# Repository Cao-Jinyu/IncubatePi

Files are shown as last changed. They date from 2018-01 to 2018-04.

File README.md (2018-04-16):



### Neonate (Newborn Child) Real Time Temperature Control Incubator

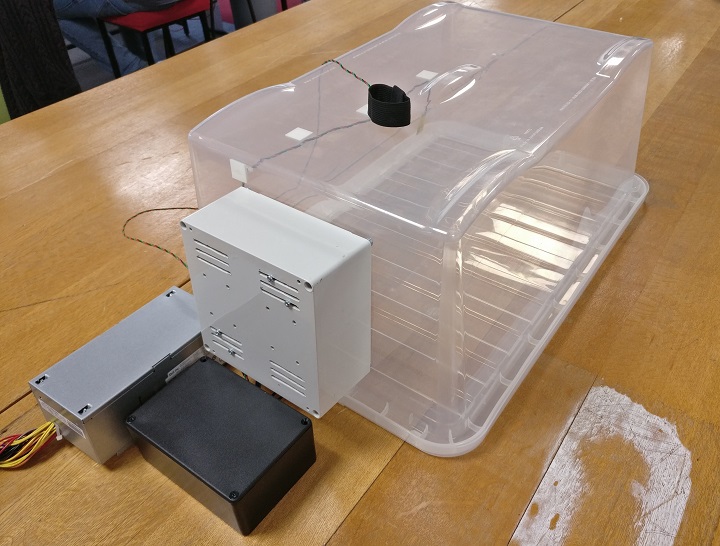
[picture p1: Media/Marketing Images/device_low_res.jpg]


*Features a Raspberry Pi, Temperature Sensors, a Heater and a Fan.*  
*Low budget alternative to conventional incubators suitable for the developing world.*

**Find our promotional video on YouTube:** http://www.youtube.com/watch?v=8vy_HCOcaGk  
**You can also find a demonstration of the device here:** https://www.youtube.com/watch?v=y4fZthFY24Q

[facebook_icon]: https://raw.githubusercontent.com/croaljack0/IncubatePi/master/Media/Marketing%20Images/facebook_icon.png
[facebook_url]: https://www.facebook.com/IncuPi/
[instagram_icon]: https://raw.githubusercontent.com/croaljack0/IncubatePi/master/Media/Marketing%20Images/instagram_icon.png
[instagram_url]: https://www.instagram.com/incupi_project
[youtube_icon]: https://raw.githubusercontent.com/croaljack0/IncubatePi/master/Media/Marketing%20Images/youtube_icon.png
[youtube_url]: https://www.youtube.com/channel/UCyrm2wJSCseUDFAKD9X7mjQ
Click these icons to follow us on  [][facebook_url] &nbsp; [][instagram_url] &nbsp; [][youtube_url]

View our project on Hackaday: https://hackaday.io/project/125376-incupi

## Problem

Premature or ill neonates often require automated temperature monitoring and control because they are unable to properly regulate their own body temperature. This is conventionally provided using expensive incubator systems. In the developing world, where standards of health care are poor and funding is very limited, an incubator solution using inexpensive and widely accessible technology is required.

## Solution

IncuPi provides a neonate temperature monitoring solution using a Raspberry Pi as the central control unit. Multiple temperature sensors provide information about the temperature of the neonate and the incubator ambient temperature. Embedded PID control software on the Raspberry Pi is then used to control a heater and fan system. This provides the appropriate heat control to ensure a neonate body temperature of 37 degrees Celsius.

**SEE THE WIKI DOCS [HERE](https://github.com/croaljack0/IncubatePi/wiki) FOR DETAILED HARDWARE AND SOFTWARE IMPLEMENTATION**

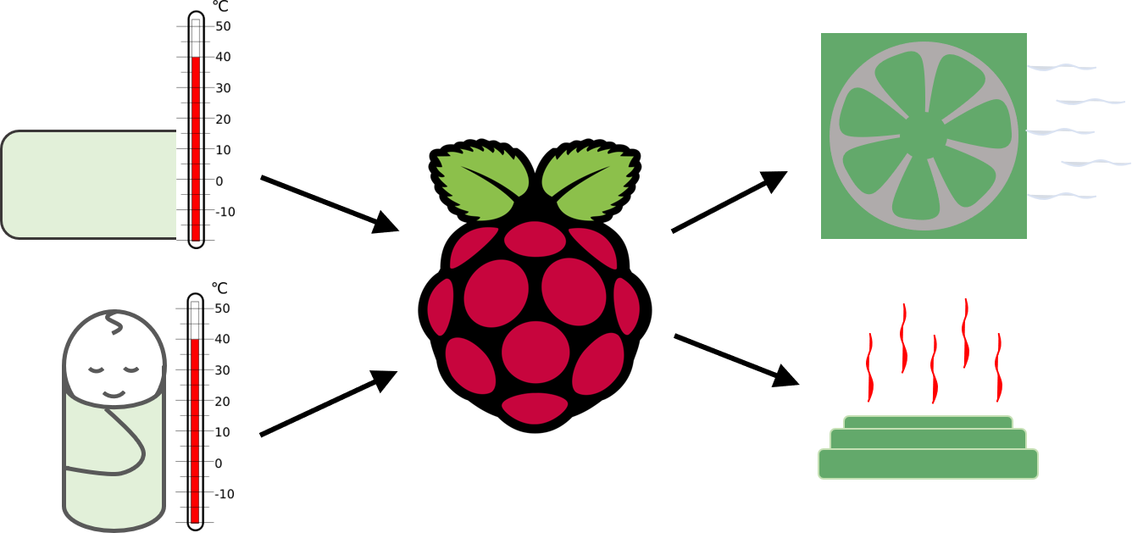
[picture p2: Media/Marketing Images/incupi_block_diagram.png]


## Real-time evaluation

#### 1. Responsiveness of the application
A fast temperature response was required to ensure fast-heating of the incubator in emergency situations. The final device was successful in achieving this. The PID temperature response times are shown below:

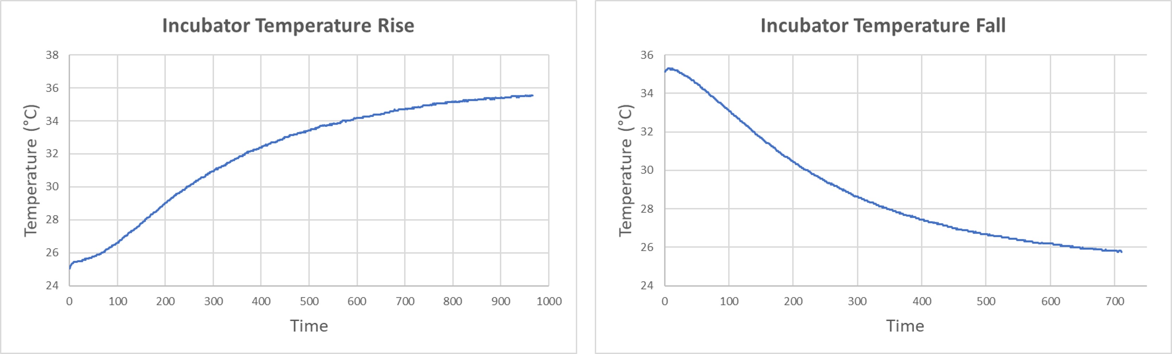
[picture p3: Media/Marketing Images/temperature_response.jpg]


The full data for these results can be found [HERE](./Experimental%20Data).

#### 2. Permitted latencies
The latency between the temperature reading and the incubator temperature change has been tested to be no longer than one minute for temperature changes of one degree Celsius.

#### 3. Sampling rate
The ambient temperature of the incubator is sampled and processed every 10 seconds by the PID control software. The neonate temperature is sampled every minute because this temperature does not vary significantly over short periods of time. This ensures sufficient data for the temperature control, modifying the heater/fan power every 5 seconds.

#### 4. Bus protocol
The Raspberry Pi communicates with the DS18B20 temperature sensors using the RPI's 1-wire interface. This uses a single wire to provide data, and power. This reduces wiring complexity and allows for multiple temperature devices connected in parallel without a chip select line for each, thus improving the flexibility and scalability.

A standard PWM signal is used to control the fan.

#### 5. How many channels
Multiple temperature sensor channels can be connected to the Raspberry Pi using the 1-wire interface. The default for this is 2: one for neonate temperature and one for the incubator ambient temperature. This is passed to the GPIO and PWM outputs to control the heating element's MOSFET and the fan respectively.

#### 6. Low level implementation: kernel or user space?
The main application runs in user space because it provides security and portability. The timing requirements of the system were not severe enough to warrant custom kernel routines. Some of the external interfaces (eg. 1-wire) are implemented using loadable kernel modules.

#### 7. Data flow from hardware to GUI to output
The Raspberry Pi sends data to a connected monitor, using QT for the display output. The Raspberry Pi is connected to the monitor using it's built-in VGA connection with an HDMI adapter.

#### 8. Buffering of data
The temperature data is buffered over a maximum of 5 minutes to aid in the accurate PID control of the slow-changing temperature values.

#### 9. Buffering impacting on the real-time performance
The buffering of the temperature values is a low performance activity, and introduces very little latency within the application.

#### 10. Post-processing of data, latencies and processor load
The data is processed real-time as the temperature information is detected. This is post-processed in by the custom PID controller to provide the values for the heater and fan elements. This introduces a maximum latency of 5 ms, allowing for low-latency temperature changes.

#### 11. Number of threads and load be distribution
The main software is executed in one thread, and child threads are created to handle the temperature measurements and other external interrupts. The number of child threads created can be varied depending on the number of temperature sensors connected, to aid in the scalability of the application.

#### 12. GUI implementation
The GUI is implemented using QT, and is displayed on a connected monitor. The refresh rate is equal to the temperature sensor sample rate: refresh every second. The allowed latency is 0.5 seconds. The temperature information is displayed real-time, along with the PID temperature controller data. This can be viewed in the [Software wiki](https://github.com/croaljack0/IncubatePi/wiki/Software).

#### 13. Class structure and unit tests
The software features a main class and 4 other classes as follows:

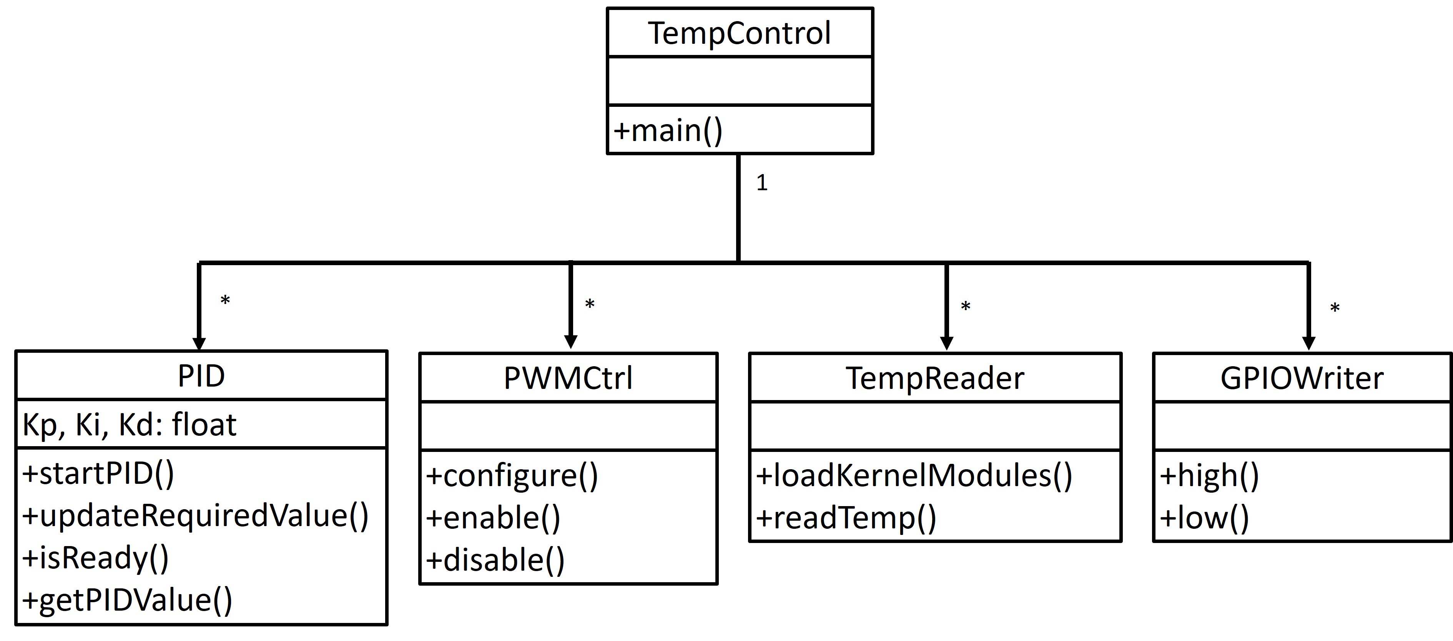
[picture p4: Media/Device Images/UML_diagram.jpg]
UML diagram


Unit tests are included for each class, and can be executed using the command `make test` within the software directory.

**SEE THE WIKI DOCS FOR DETAILS ON SOFTWARE [HERE](https://github.com/croaljack0/IncubatePi/wiki/Software)**

#### 14. Team structure
The team members and roles are as follows:

* **Jack Croal** - Hardware Developer
* **Chris Brown** - Software Developer
* **Cameron Houston** - GUI Implementation

These roles are flexible, with every team member cooperating on each section of the project to improve the common understanding within the team. Three times weekly scrum meetings are carried out to establish roles and tasks.

#### 15. Project time allocation
This project was completed over 4 months.

* **January**: Research and initial experimental development
* **February**: Hardware manufacturing and software implementation
* **March**: Finalising of software and incubator experimental tests
* **April**: Completion of project with release and media engagement

#### 16. Version control
The git version control software was chosen due to its wide-scale use and support, and its ability to merge between branches and create releases. The software releases can be found in the [releases section](https://github.com/croaljack0/IncubatePi/releases) of this GitHub, labeled A.B where A is the major release number and B is the minor release number.

#### 17. Release strategy and publication
[facebook_icon]: https://raw.githubusercontent.com/croaljack0/IncubatePi/master/Media/Marketing%20Images/facebook_icon.png
[facebook_url]: https://www.facebook.com/IncuPi/
[instagram_icon]: https://raw.githubusercontent.com/croaljack0/IncubatePi/master/Media/Marketing%20Images/instagram_icon.png
[instagram_url]: https://www.instagram.com/incupi_project
[youtube_icon]: https://raw.githubusercontent.com/croaljack0/IncubatePi/master/Media/Marketing%20Images/youtube_icon.png
[youtube_url]: https://www.youtube.com/channel/UCyrm2wJSCseUDFAKD9X7mjQ
Click these icons to follow us on  [][facebook_url] &nbsp; [][instagram_url] &nbsp; [][youtube_url]

The project can also be found on Hackaday here: https://hackaday.io/project/125376-incupi

The software and hardware schematics are released here on GitHub. Please feel free to download, under the MIT license included.

#### 18. Success of the application
The application is evaluated on its temperature response time based on the neonate's temperature changes. The experimental results are included [HERE](./Experimental%20Data). The application is successful in holding a steady temperature within the incubator and changes the temperature accordingly with low latency and useful graphical output.

Overall, this project demonstrates a key understanding of real-time applications, and follows a clear software life-cycle using proper software development techniques.

## University of Glasgow
Developed as part of Real Time Embedded Programming Project at the University of Glasgow.

Course convener:    Dr Bernd Porr

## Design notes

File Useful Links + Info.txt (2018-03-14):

Incubator Information:
http://www.d4surgicals.com/Infant-Incubator/index.htm

Adafruit temperature sensor document
https://cdn-learn.adafruit.com/downloads/pdf/adafruits-raspberry-pi-lesson-11-ds18b20-temperature-sensing.pdf

http://www.jumpnowtek.com/rpi/Using-the-Raspberry-Pi-Hardware-PWM-timers.html

http://librpip.frasersdev.net/peripheral-config/pwm0and1/

https://sites.google.com/site/semilleroadt/raspberry-pi-tutorials/gpio

ssh -X team10@rank510iot.eng.gla.ac.uk

ssh -X pi@192.168.1.181

git config --global http.proxy http://wwwcache.gla.ac.uk:8080

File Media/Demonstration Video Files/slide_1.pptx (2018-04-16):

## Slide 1

FINAL DEVICE
      - Heating Element
      - Fan
      - Temperature Sensors
      - Modular Enclosures

A picture containing object Description generated with very high confidence

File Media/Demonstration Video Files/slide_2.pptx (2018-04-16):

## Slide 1

PWM Fan Operation
- Adjusts automatically to temperature fluctuations
- Disperses heat through incubator

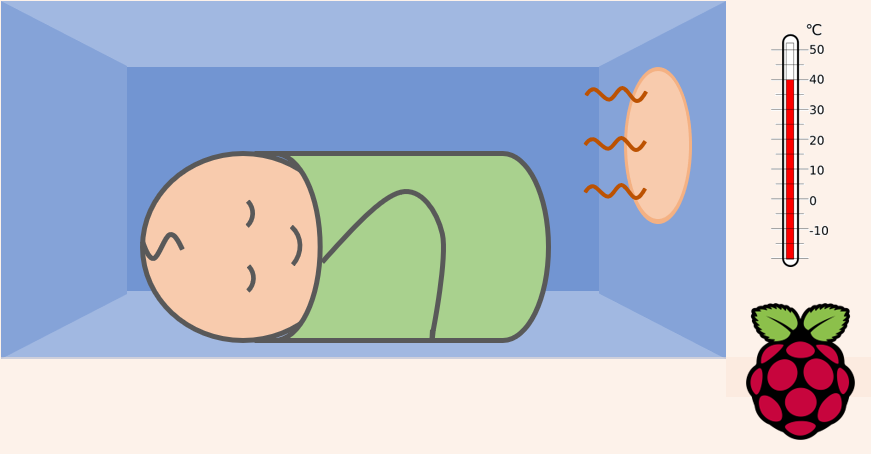
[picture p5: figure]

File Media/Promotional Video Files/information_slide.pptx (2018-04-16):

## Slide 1

For more information:
Follow IncuPi on and
Find our GitHub repository for source code
and device construction:
https://github.com/croaljack0/IncubatePi

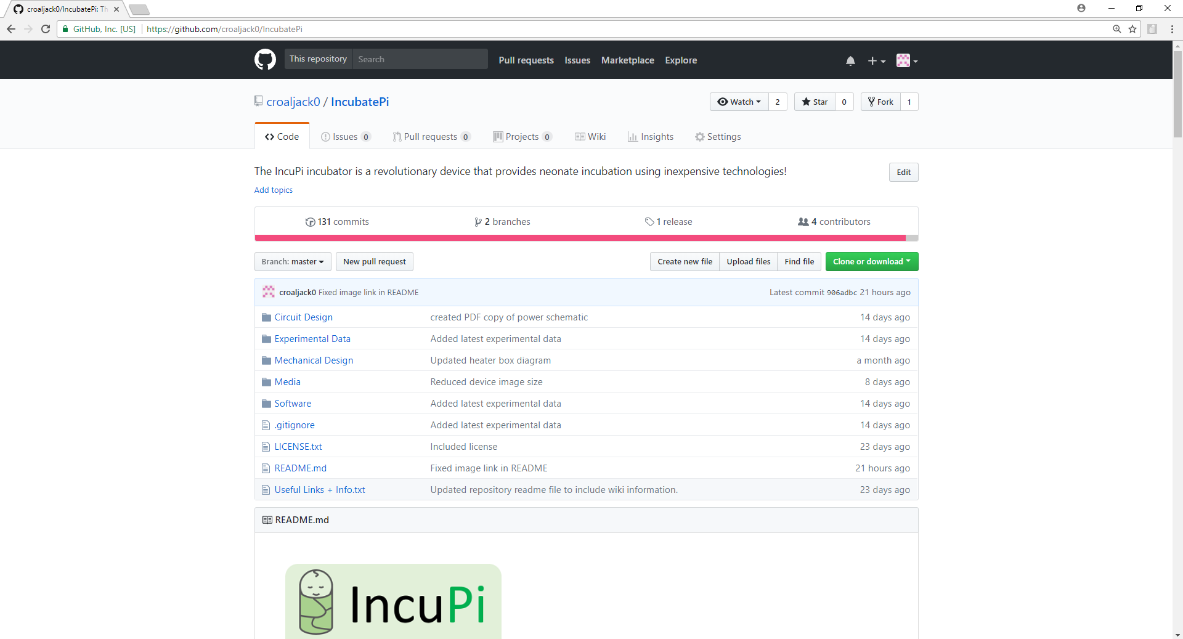
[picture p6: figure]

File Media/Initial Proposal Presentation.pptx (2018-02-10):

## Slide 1

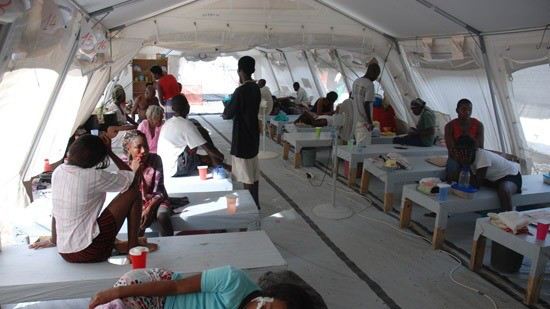
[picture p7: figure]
Image result for third world medicine

IncuPi

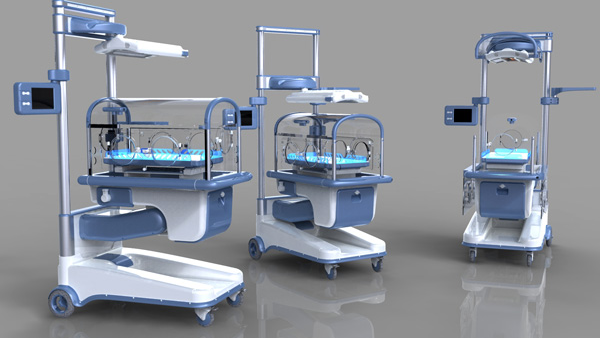
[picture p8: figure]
Image result for incubator neonate

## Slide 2

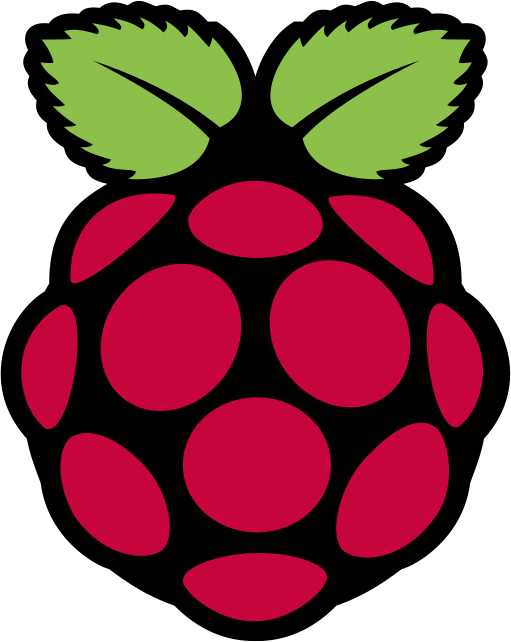
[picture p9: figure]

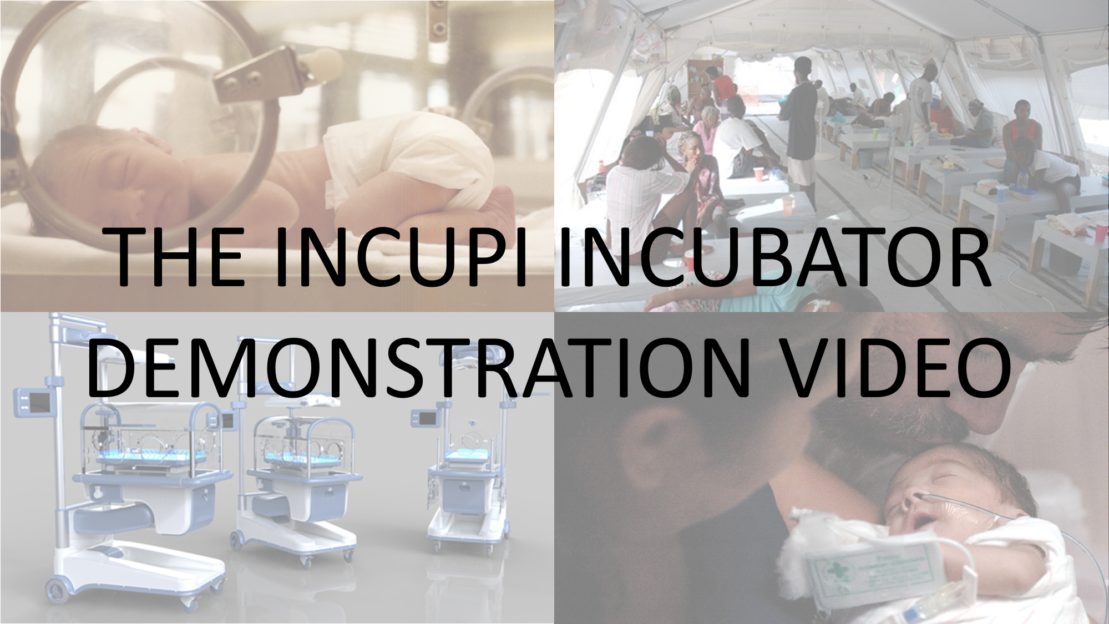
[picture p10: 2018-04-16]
Media/Demonstration Video Files/first_slide.png

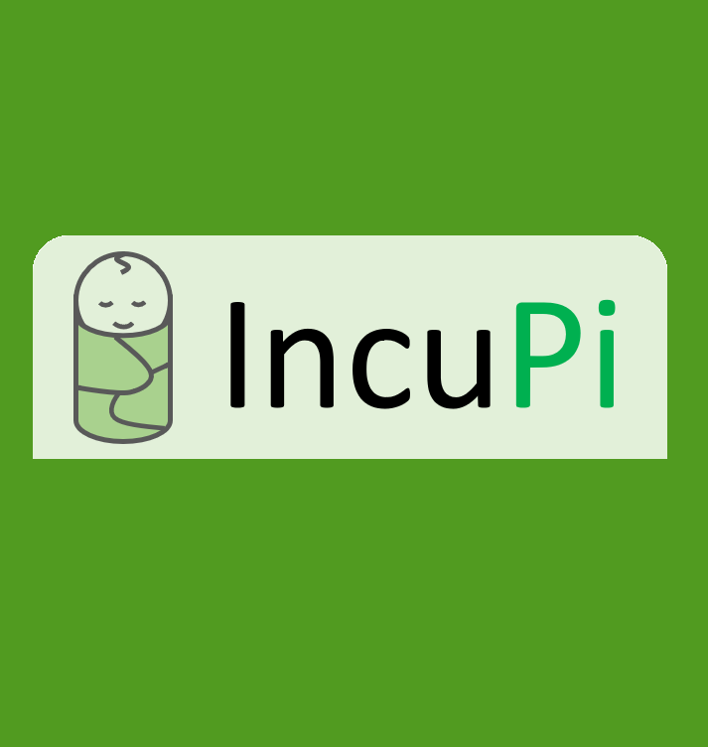
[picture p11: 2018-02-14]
Media/Marketing Images/facebook_profile.png

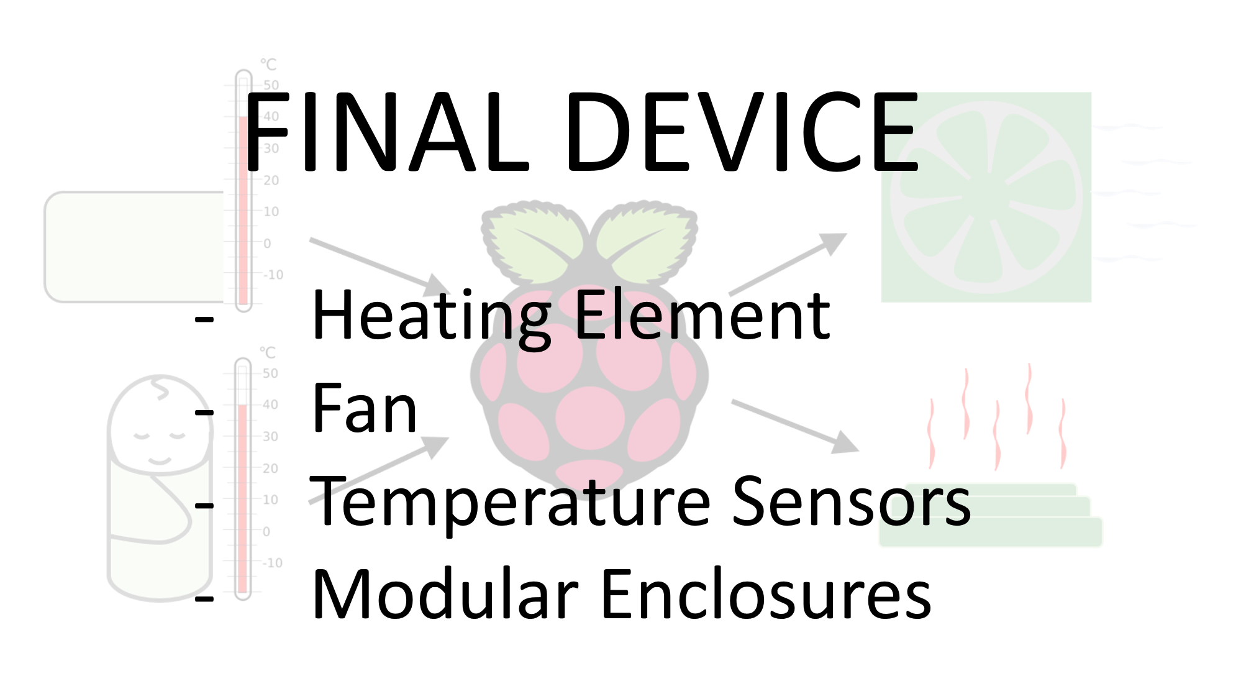
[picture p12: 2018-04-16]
Media/Demonstration Video Files/slide_1.png

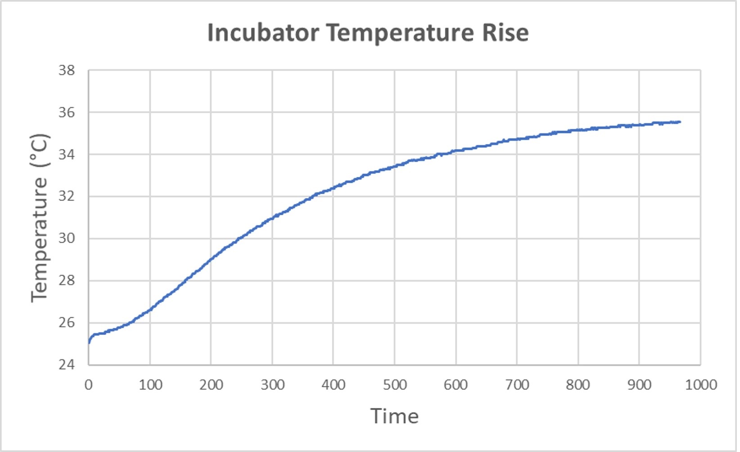
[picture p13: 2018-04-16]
Media/Promotional Video Files/temperature_response_rise.jpg

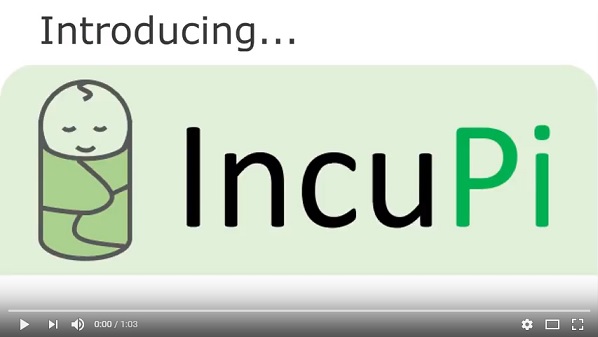
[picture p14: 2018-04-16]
Media/Promotional Video Files/video_thumbnail.jpg

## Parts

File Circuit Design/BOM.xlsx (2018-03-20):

 | Key | Aquired |  | Additionally required : | Selection of Wires
 |  | Ordered |  |  | Monitor & Keyboard
 |  | Not Ordered |  |  | Selections of Screws & Spacers
Required | Unit Cost | Total Cost | Item Description | Manufacturer | Manufacturer Part No. | Supplier | Supplier Part No | URL
1 | £32.95 | £32.95 | Rasberry Pi 3 | Raspberry Pi | Model B | Amazon | B01CD5VC92 | https://www.amazon.co.uk/Raspberry-Pi-Model-Quad-Motherboard/dp/B01CD5VC92
1 | £17.49 | £17.49 | Case Fan 120 mm | Noctua | NF-F12PWM | Amazon | B00650P2ZC | https://www.amazon.co.uk/Noctua-NF-F12PWM-Case-Fan-120/dp/B00650P2ZC
2 | £3.98 | £7.96 | Temperature Sensor | Maxim | DS18B20U+ | RS | 732-7490 | https://uk.rs-online.com/web/p/temperature-humidity-sensors/7327490/
1 | £7.00 | £7.00 | 45 Litre Plastic Box | Wham | 10870 | Tesco | n/a | n/a
1 | £1.71 | £1.71 | Elastic | The Cut & Sew Comp. | ELA25-0721BLK | Amazon | B00U8THDR6 | https://www.amazon.co.uk/Elastic-Smooth-Durable-Quality-Metres/dp/B00U8THDR6
1 | £21.49 | £21.49 | ABS Enclosure | Hammond | 1554SGY | RS | 818-0457 | https://uk.rs-online.com/web/p/general-purpose-enclosures/8180457/
1 | £6.14 | £6.14 | 12 V 150 W Heater | Adhere To Fly | n/a | Amazon | B01N0Q9RQ4 | https://www.amazon.co.uk/Adhere-Fly-Aluminum-Thermostat-Temperature/dp/B01N0Q9RQ4
2 | £0.36 | £0.72 | 2 Pos Header MF | Molex | 0039281023 | Digi-key | WM3843-ND | https://www.digikey.co.uk/product-detail/en/molex-llc/0039293026/WM3843-ND/2002650
2 | £0.198 | £0.40 | 2 Pos Receptacle MF | Molex | 39-01-2020 | RS | 484-1748 | https://uk.rs-online.com/web/p/pcb-connector-housings/4841748/
4 | £0.037 | £0.15 | Mini-fit Jr Crimp | Molex | 39-00-0038 | RS | 670-6307 | https://uk.rs-online.com/web/p/pcb-connector-contacts/6706307/
1 | £0.30 | £0.30 | Asym 4 Pin Header | Molex | 470531000 | Digi-key | WM4330-ND | https://www.digikey.co.uk/product-detail/en/molex-llc/0470531000/WM4330-ND/2421261
15 | £0.11 | £1.65 | Standard Crimps | Molex | 08-50-0114 | Digi-key | WM1114-ND | https://www.digikey.co.uk/product-detail/en/molex-llc/08-50-0114/WM1114-ND/26475
2 | £0.16 | £0.32 | 3 Pos Header | Molex | 22232031 | Digi-key | WM4201-ND | https://www.digikey.co.uk/product-detail/en/molex-llc/0022232031/WM4201-ND/26669
2 | £0.12 | £0.24 | 3 Pos Receptacle | Molex | 22012037 | Digi-key | WM2012-ND | https://www.digikey.co.uk/product-detail/en/molex-llc/0022012037/WM2012-ND/171992
1 | £0.54 | £0.54 | 4 Pos Mini-fit Header | Molex | 39281043 | Digi-key | WM3801-ND | https://www.digikey.co.uk/product-detail/en/molex-llc/0039281043/WM3801-ND/61400
1 | £0.37 | £0.37 | N-Channel Mosfet | TSC | TSM4806CS RLG | Digi-key | TSM4806CSRLGCT-ND | https://www.digikey.co.uk/product-detail/en/taiwan-semiconductor-corporation/TSM4806CS-RLG/TSM4806CSRLGCT-ND/7360374
1 | £0.42 | £0.42 | Mosfet Driver | Diodes Inc. | ZXGD3003E6TA | Digi-key | ZXGD3003E6CT-ND | https://www.digikey.co.uk/product-detail/en/diodes-incorporated/ZXGD3003E6TA/ZXGD3003E6CT-ND/1827766
2 | £0.11 | £0.22 | 2 Pos Header | Molex | 22-23-2021 | Digi-key | WM4200-ND | https://www.digikey.co.uk/product-detail/en/molex-llc/22-23-2021/WM4200-ND/26667
2 | £0.09 | £0.18 | 2 Pos Receptacle | Molex | 22-01-3027 | Digi-key | WM2000-ND | https://www.digikey.co.uk/product-detail/en/molex-llc/22-01-3027/WM2000-ND/26431
2 | £0.34 | £0.68 | 40 Pin GPIO header | On Shore Tech | 302-S401 | Digi-key | ED10529-ND | https://www.digikey.co.uk/product-detail/en/on-shore-technology-inc/302-S401/ED10529-ND/2794240
2 | £1.17 | £2.34 | 40 Pin Ribbon Cable | Assmann WSW | H3CCS-4006G | Digi-key | H3CCS-4006G-ND | https://www.digikey.co.uk/product-detail/en/assmann-wsw-components/H3CCS-4006G/H3CCS-4006G-ND/1218595
 | Total | £70.31

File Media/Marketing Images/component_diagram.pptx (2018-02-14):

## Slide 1


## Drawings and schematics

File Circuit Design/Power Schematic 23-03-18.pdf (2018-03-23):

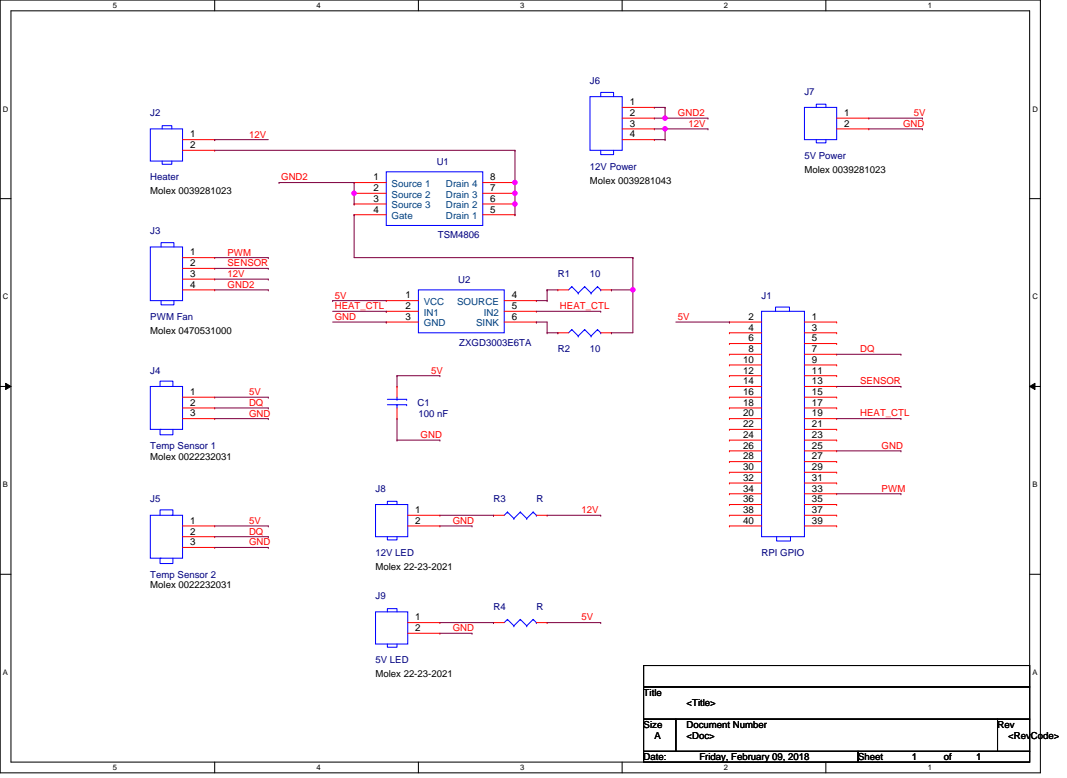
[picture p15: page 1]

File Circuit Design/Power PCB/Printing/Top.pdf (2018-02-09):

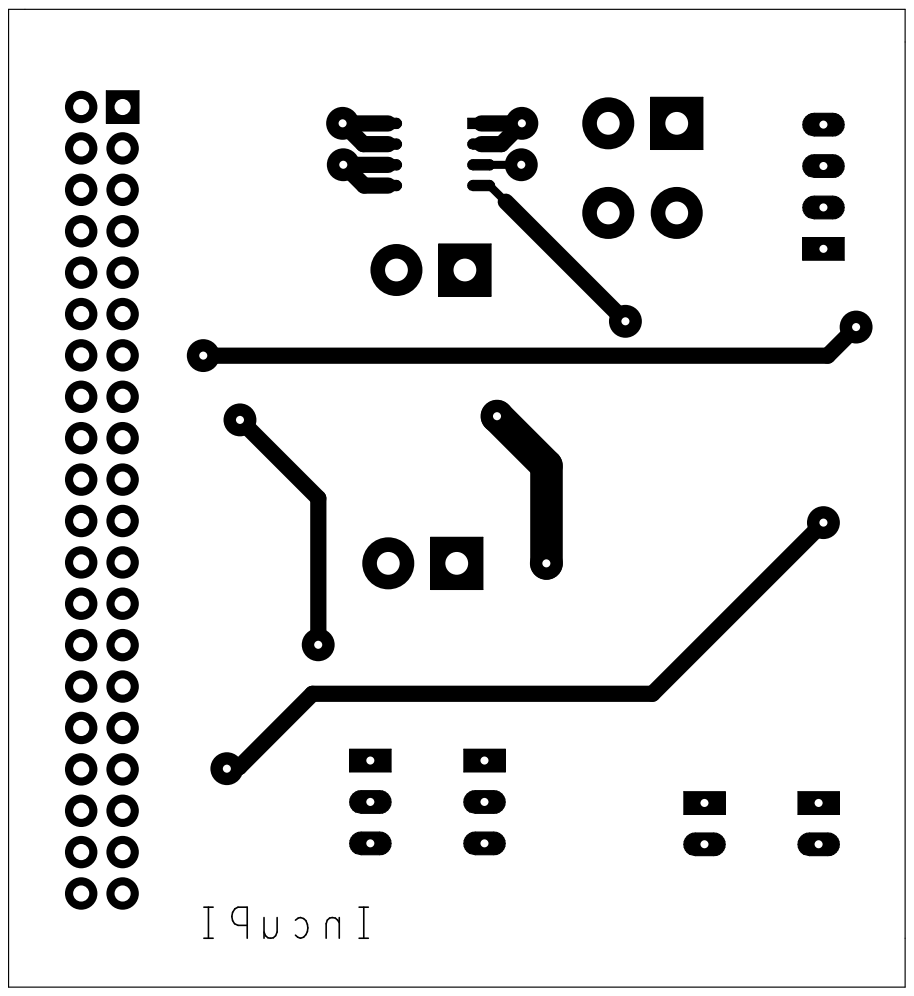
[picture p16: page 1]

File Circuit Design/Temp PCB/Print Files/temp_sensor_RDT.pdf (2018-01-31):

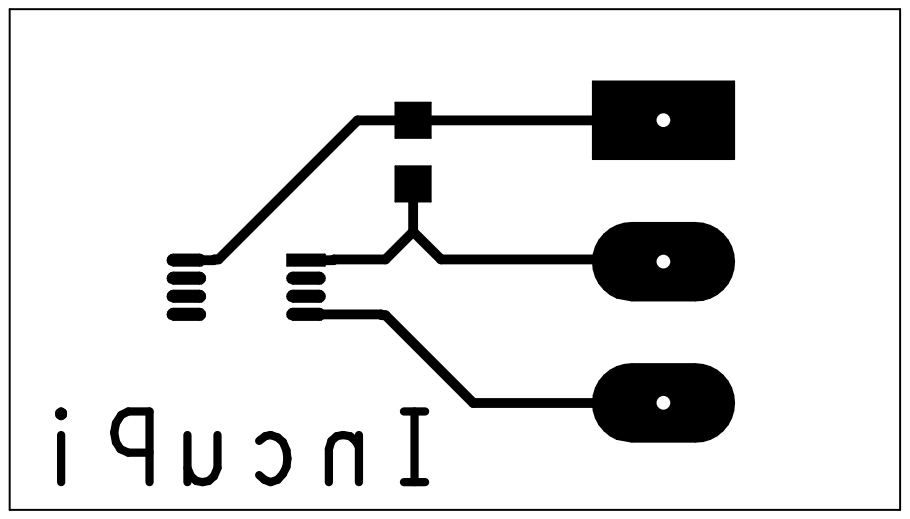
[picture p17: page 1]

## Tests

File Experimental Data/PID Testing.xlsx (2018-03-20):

 | Run 1 |  | Run 2 |  | Run 3 |  | Run 4
P | 0.12 |  | 0.16 |  | 0.14 |  | 0.146
D | 0.16 |  | 0.5 |  | 0.16 |  | 0.16
I | 0.00055 |  | 0.00055 |  | 0.00055 |  | 0.0006
C | 0 |  | 0 |  | 0.1 |  | 0
 | 23.437 | 0 | 22.812 | 0 | 25.062 | 0 | 24.312 | 0
 | 23.5 | 0.5688 | 23 | 1 | 25.125 | 0.746 | 24.437 | 1
 | 23.562 | 0.5688 | 23.062 | 1 | 25.187 | 0.746 | 24.562 | 1
 | 23.562 | 0.5688 | 23.125 | 1 | 25.187 | 0.746 | 24.562 | 1
 | 23.625 | 0.5688 | 23.187 | 1 | 25.25 | 0.746 | 24.625 | 1
 | 23.625 | 0.5688 | 23.25 | 1 | 25.25 | 0.746 | 24.687 | 1
 | 23.687 | 0.5688 | 23.312 | 1 | 25.25 | 0.746 | 24.75 | 1
 | 23.625 | 0.469244 | 23.375 | 0.958197 | 25.25 | 0.663625 | 24.75 | 1
 | 23.687 | 0.469244 | 23.437 | 0.958197 | 25.25 | 0.663625 | 24.812 | 1
 | 23.687 | 0.469244 | 23.5 | 0.958197 | 25.25 | 0.663625 | 24.875 | 1
 | 23.75 | 0.469244 | 23.5 | 0.958197 | 25.187 | 0.663625 | 24.875 | 1
 | 23.75 | 0.469244 | 23.562 | 0.958197 | 25.187 | 0.663625 | 24.937 | 1
 | 23.75 | 0.469244 | 23.687 | 0.958197 | 25.187 | 0.663625 | 25 | 1
 | 23.75 | 0.483252 | 23.687 | 0.923798 | 25.187 | 0.698424 | 25 | 1
 | 23.75 | 0.483252 | 23.75 | 0.923798 | 25.187 | 0.698424 | 25.062 | 1
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

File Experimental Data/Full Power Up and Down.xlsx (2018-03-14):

P: 40000 | P: 40000
DC: 20000 | DC: 40000
25.062 | 35.125
25.187 | 35.187
25.25 | 35.25
25.312 | 35.25
25.312 | 35.312
25.375 | 35.312
25.375 | 35.312
25.375 | 35.312
25.437 | 35.25
25.437 | 35.312
25.437 | 35.25
25.437 | 35.312
25.437 | 35.25
25.437 | 35.25
25.437 | 35.25
25.437 | 35.187
25.5 | 35.187
25.5 | 35.187
25.5 | 35.187
25.5 | 35.187
25.5 | 35.125
25.5 | 35.125
25.5 | 35.125
25.5 | 35.062
25.5 | 35.062
25.5 | 35.062
25.562 | 35.062
25.562 | 35
25.562 | 35
25.562 | 35
25.562 | 34.937
25.625 | 34.937
25.562 | 34.937
25.625 | 34.875
25.625 | 34.875
25.625 | 34.875
25.625 | 34.812
25.625 | 34.812
25.625 | 34.812
25.625 | 34.75
25.687 | 34.75
25.687 | 34.687
25.687 | 34.687
25.687 | 34.687
25.687 | 34.687
25.687 | 34.625
25.75 | 34.562
25.75 | 34.562
25.75 | 34.562
25.75 | 34.5
25.75 | 34.5
25.75 | 34.437
25.812 | 34.437
25.812 | 34.437
25.812 | 34.375
25.812 | 34.312
25.875 | 34.312
25.875 | 34.312
25.875 | 34.25
25.875 | 34.25
25.875 | 34.187
25.875 | 34.187
25.937 | 34.187
25.937 | 34.125
25.937 | 34.125
26 | 34.062
26 | 34.062
26 | 34.062
26 | 34
26 | 33.937
26.062 | 33.937
26.062 | 33.875
26.062 | 33.875
26.125 | 33.875
26.125 | 33.812
26.187 | 33.812
26.187 | 33.75
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

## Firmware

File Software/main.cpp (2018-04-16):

#include <stdlib.h>
#include <string>
#include <iostream>
#include <fstream>
#include <signal.h>
#include <thread>
#include <chrono>
#include "PWMCtrl.hpp"
#include "GPIOWriter.hpp"
#include "TempReader.hpp"
#include "PID.hpp"
#include "window.hpp"
#include <QApplication>

/*
    This code is intended for execution on a RPI 3 Model B running Raspbian.

    In order for this code to execute correctly the linux kernel version must be at least 4.9.
    This can be checked by executing the command:   uname -r

    Additionally the file: /boot/config.txt
    must contain the line: dtoverlay=pwm,pin=19,func=2
    to configure BCM pin 19 (GPIO 35) so that it can be used for PWM for the fan control.

    The temp sensor unique identity codes NEONATE_TEMP_SENSOR and AMBIENT_TEMP_SENSOR must be
    set to match the DS18B20 devices being used.
*/

static std::string NEONATE_TEMP_SENSOR = "28-000005f50d4c";    // Unique identity code of DS18B20 temp sensor being used to measure neonate temperature
static std::string AMBIENT_TEMP_SENSOR = "28-000005f4e7d6";    // Unique identity code of DS18B20 temp sensor being used to measure ambient temperature

static const int PWMCHIP = 1;                   // PWM chip on the RPI that will be used to control the fan (PWM chip 1 is connected to GPIO pins 33 and 35)
static const int HEATER_BCM_PIN = 10;           // BCM Pin on the RPI that the heater will be connected to (BCM pin 10 is connected to GPIO pin 19)
static const int DEFAULT_PERIOD = 40000;        // Default period that will be used for the fan PWM control (nanoseconds)
static const int DEFAULT_DUTY_CYCLE = 40000;    // Default duty cycle that will be used for the fan PWM control (nanoseconds)
static const int HEATER_PERIOD = 10;            // Period of heater PWM (seconds)

static const float NEONATE_IDEAL_MIN = 36.5;    // Lower boundary of the neonate ideal body temperature range (°C)
static const float NEONATE_IDEAL_MAX = 37.2;    // Higher boundary of the neonate ideal body temperature range (°C)
static const float MIN_AMBIENT_TEMP = 25.0;     // Minimum allowed target ambient temperature(°C)
static const float MAX_AMBIENT_TEMP = 36.0;     // Maximum allowed target ambient temperature (°C)
static const float INITIAL_TARGET = 26.0;       // Initial ambient temperature target (°C)
static const int TEMP_READ_DELAY = 60;          // Delay between neonate temperature readings (seconds)

static const int SUCCESS = 0;                   // Used to indicate that the program has so far executed correctly
static const int FAILURE = 1;                   // Used to indicate that the program has not executed correctly in some way
static int success = SUCCESS;                   // Used to indicate wether the execution of the program has been successful

static std::string OUTFILE = "results.txt";     // File where program output will be written to
static std::ofstream outfile;
static float heater_pwm_duty_cycle = 0;

static const int MIN_PID = 0;           // The minimum possible value of the PID output
static const int MAX_PID = 1;           // The maximum possible value of the PID output
static const int SAMPLE_TIME = 10;      // The time between PID iterations (seconds)
static const float P_COEFF = 0.14600;   // PID proportional coefficient
static const float D_COEFF = 0.16000;   // PID differential coefficient
static const float I_COEFF = 0.00060;   // PID integral coefficient

static PWMCtrl *pwm;            // Fan control object
static GPIOWriter *heater;      // Heater control object
static TempReader *neonate;     // Neonate temperature sensor control object
static TempReader *ambient;     // Ambient temperature sensor control object

/*
    Concrete implementation of the abstract class PID which implements the
    get_current_value() function by reading the current ambient temperature.
*/
class AmbientTempPID : public PID {

    using PID::PID;
    private:
        float get_current_value(){ return ambient->readTemp(); }
};

static AmbientTempPID *ambient_temp_pid; // Ambient temperature PID controller

/*
    Controls the heater PWM signal according to the PID specified duty cycle.
    The duty cycle is specified as a proportion (between 0 and 1) by variable heater_pwm_duty_cycle.
    (Intended for execution in a seperate thread as it contains an infinite loop.)
*/
void heater_pwm(){

    int period_ms, on_time_ms, off_time_ms;

    while(true){

        // Check if the output value of the PID controller is ready to be read.
        if (ambient_temp_pid->isReady())

            // Update the pwm duty cycle based on the current PID controller output.
            heater_pwm_duty_cycle = ambient_temp_pid->get_pid_value();

        // Calculate PWM on and off times base on period and duty cycle
        period_ms = HEATER_PERIOD * 1000;
        on_time_ms = period_ms * heater_pwm_duty_cycle;
        off_time_ms = period_ms - on_time_ms;

        // Set the heater high and low accordingly
        heater->high();
        std::this_thread::sleep_for(std::chrono::milliseconds(on_time_ms));
        heater->low();
        std::this_thread::sleep_for(std::chrono::milliseconds(off_time_ms));

    }
}

/*
    Updates the target ambient temperature based on the current neonate baby temperature.
    (Intended for execution in a seperate thread as it contains an infinite loop.)
*/
void ambient_target_select(){

    float neonate_temp;
    float target_ambient_temp = INITIAL_TARGET;

    while (true){

        // Allow time for the temperature sensor to heat to the neonates body temperature.
        std::this_thread::sleep_for(std::chrono::seconds(TEMP_READ_DELAY));

        // Get neonate temperatrue
        neonate_temp = neonate->readTemp();

        // If the neonate temperature is outwith of the ideal range, increment or decrement the target ambient temperature accordingly
        // while ensuring it does not go outwith specified limits.
        if (neonate_temp < NEONATE_IDEAL_MIN && target_ambient_temp < MAX_AMBIENT_TEMP) target_ambient_temp++;
        else if (neonate_temp > NEONATE_IDEAL_MAX && target_ambient_temp > MIN_AMBIENT_TEMP) target_ambient_temp--;

        // Update the PID controller to the new target
        //ambient_temp_pid->update_required_value(target_ambient_temp);
        //std::cout << "Current Neonate Temperature: " << neonate_temp << std::endl;
        //std::cout << "Target Ambient Temperature: " << target_ambient_temp << std::endl;
    }

}

/*
    Ensures that all created objects are properly decommisioned prior to exiting the program.
    Updates the current success status of execution (either SUCCESS or FAILURE).
*/
void exit_gracefully(int signum){

    std::cout << std::endl << "Exiting...." << std::endl;

    try{

        if (pwm){
            pwm->disable(); // Disables the fan
            delete pwm;
        }
        if (heater){
            heater->low(); // Turns of the heater
            delete heater;
        }
        delete neonate;
        delete ambient;
        delete ambient_temp_pid;

        if (outfile.is_open()) outfile.close();

    } catch(std::runtime_error& e){
        std::cout << e.what() << std::endl;
        success = FAILURE; // The execution is considered a failure if any exceptions were thrown.
    }

    if (success == SUCCESS)
        std::cout << "Program executed successfully" << std::endl;
    else
        std::cout << "Program execution failed" << std::endl;

    exit(success);
}

int main(int argc, char *argv[]){

    // Register a signal handler so that the program can exit correctly if a ctl-c signal is received.
    signal(SIGINT, exit_gracefully);

    try{

        // Create a new PWMCtl object to control the fan, set the default period and duty cycle, and enable.
        pwm = new PWMCtrl(PWMCHIP);
        pwm->configure(DEFAULT_PERIOD,DEFAULT_DUTY_CYCLE);
        pwm->enable();

        // Configure a GPIO pin to control the heater
        heater = new GPIOWriter(HEATER_BCM_PIN);

        // Load the neccessary linux kernal modules and then configure two temp sensors.
        TempReader::loadKernelModules();
        neonate = new TempReader(NEONATE_TEMP_SENSOR);
        ambient = new TempReader(AMBIENT_TEMP_SENSOR);

    } catch(std::exception& e){
        // Program exits if any exceptions are detected.
        std::cout << e.what();
        success = FAILURE;
        exit_gracefully(0);
    }

    // Open file to write program output to.
    outfile.open(OUTFILE.c_str());

    // Create an ambient temperature PID controller and set it to start iterating.
    ambient_temp_pid = new AmbientTempPID(SAMPLE_TIME, INITIAL_TARGET, MIN_PID, MAX_PID, P_COEFF, I_COEFF, D_COEFF);
    ambient_temp_pid->start_pid();

    // Start a thread that controls the heater PWM signal according to the PID output.
    std::thread heater_thread(heater_pwm);

    // Start a thread which monitors the neonate temperature and sets the target ambient temperature.
    std::thread temperature_thread(ambient_target_select);

    //Start a thread which displays a QT window for control ofthe application
    QApplication app(argc, argv);
    Window window(ambient_temp_pid, ambient);
    window.showMaximized();

    // call the window.timerEvent function every 40 ms and begin execution
    window.startTimer(40);
    app.exec();

    while(true) {

        std::cout << ambient->readTemp() << ", " << heater_pwm_duty_cycle << std::endl;
        outfile << ambient->readTemp() << ", " << heater_pwm_duty_cycle << std::endl;

    }
}

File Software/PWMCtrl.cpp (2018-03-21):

#include <iostream>
#include <fstream>
#include <string>
#include <stdio.h>
#include <stdlib.h>
#include "PWMCtrl.hpp"

static std::string EXPORTFILE = "/sys/class/pwm/pwmchip0/export";   // Linux system file which is written to in order to export a PWM chip.
static std::string BASEFILE = "/sys/class/pwm/pwmchip0/pwm";        // This is combined with a chip number to form the directory where the PWM files associated with that chip are found.
static std::string PERIODFILE = "/period";                          // Can be combined with BASEFILE and a chip no. to give the name of the linux system file were the PWM period should be written to.
static std::string DUTYCYCLEFILE = "/duty_cycle";                   // As above for duty cycle.
static std::string ENABLEFILE = "/enable";                          // As above for enable.

static const int MIN_PERIOD = 10000;    // The PWM period must be at least this value in all instances.
static const int ENABLE = 1;            // Should be written to the enable file in order to enable the PWM signal.
static const int DISABLE = 0;           // Should be written to the enable file in order to disable the PWM signal.
static const int NUM_OF_CHIPS = 2;      // Number of PWM chips availible on the RPI being used.

static std::string TEMPFILE = "temp";
static std::string MODULECHECK = "lsmod | grep pwm > " + TEMPFILE;  // Linux system command which outputs any installed modules containing the string "pwm" to TEMPFILE.

PWMCtrl::PWMCtrl(int pwmchip) {

    std::ifstream tempFile;
    std::ofstream exportFile;
    std::string line;

    // Check the pwm chip number is a valid for the RPI
    if (pwmchip < 0 || pwmchip >= NUM_OF_CHIPS)
        throw std::range_error("Couldn't create PWMCtrl as chip number is invalid.");

    // Execute Linux command that writes any modules containing the string "pwm" to a file temp.
    if (system(MODULECHECK.c_str()) == -1)
        throw std::runtime_error("PWM Module Check Error: Couldn't execute lsmod linux system command.");

    // Opens the file where the output of the command was piped to.
    tempFile.open(TEMPFILE.c_str());
    if (!tempFile.is_open())
        throw std::runtime_error("PWM Module Check Error: Couldn't open command output file.");

    // Checks that the file is not empty. If it is empty the PWM kernal module has not been installed.
    if (!getline(tempFile,line)) {
        tempFile.close();
        throw std::runtime_error("PWM Module Check Error: Couldn't find the neccessary kernal modules.");
    }
    tempFile.close();

    // Open the linux PWM export file.
    exportFile.open(EXPORTFILE.c_str());
    if(!exportFile.is_open())
        throw std::runtime_error("Couldn't carry out export as couldn't open PWM export linux system file.");

    // Write out the pwmchip number to export that chip.
    exportFile << pwmchip << std::endl;
    exportFile.close();

    // Create pwm linux system file names.
    periodFileName = BASEFILE + std::to_string(pwmchip) + PERIODFILE;
    dutyCycleFileName = BASEFILE + std::to_string(pwmchip) + DUTYCYCLEFILE;
    enableFileName = BASEFILE + std::to_string(pwmchip) + ENABLEFILE;

}

void PWMCtrl::configure(int period, int dutyCycle) {

    std::ofstream periodFile;
    std::ofstream dutyCycleFile;
    std::string exceptionMessage;

    // Check that the period is valid.
    if (period < MIN_PERIOD) {
        exceptionMessage = "Invalid period. Must be greater than " + std::to_string(MIN_PERIOD);
        throw std::range_error(exceptionMessage);
    }

    // Check that the duty cycle is valid
    if (dutyCycle < 0 || dutyCycle > period)
        throw std::range_error("Invalid duty cycle. Must be between 0 and the period.");

    // Open the linux PWM period file.
    periodFile.open(periodFileName.c_str());
    if(!periodFile.is_open())
        throw std::runtime_error("Couldn't update period as couldn't open PWM period linux system file.");

    // Write out period to linux PWM period file
    periodFile << period << std::endl;
    periodFile.close();

    // Open the linux PWM duty cycle file
    dutyCycleFile.open(dutyCycleFileName.c_str());
    if(!dutyCycleFile.is_open())
        throw std::runtime_error("Couldn't update duty cycle as couldn't open PWM duty cycle linux system file.");

    // Write out duty cycle to linux PWM duty cycle file
    dutyCycleFile << dutyCycle << std::endl;
    dutyCycleFile.close();

    std::cout << "Period: " << period << ", Duty Cycle: " << dutyCycle << std::endl;

}

void PWMCtrl::enable(){

    std::ofstream enableFile;

    // Open the linux PWM enable file
    enableFile.open(enableFileName.c_str());
    if(!enableFile.is_open())
        throw std::runtime_error("Couldn't enable PWM as couldn't open PWM enable linux system file.");

    // Write out enable
    enableFile << ENABLE << std::endl;
    enableFile.close();
}

void PWMCtrl::disable(){

    std::ofstream enableFile;

    // Open the linux PWM enable file
    enableFile.open(enableFileName.c_str());
    if(!enableFile.is_open())
        throw std::runtime_error("Couldn't disable PWM as couldn't open PWM enable linux system file.");

    // Write out disable
    enableFile << DISABLE << std::endl;
    enableFile.close();

}

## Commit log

2018-01-17 Test commit on Raspberry Pi. Updated readme file.
2018-01-24 Included bill of materials and list of useful links
    [BOM.xlsx]
2018-01-24 Added temperature sensor link
    [BOM.xlsx]
2018-01-31 Included OrCAD PCB files for safe keeping
    [temp_sensor_blank.brd, temp_sensor_v1.brd, temp_sensor_v2_RDB.brd, temp_sensor_v2_RDT.brd]
2018-01-31 Included exgtra item on BOM and initial presentation file
    [BOM.xlsx]
2018-01-31 Included heater in BOM
    [BOM.xlsx]
2018-01-31 Included relay module in BOM
    [BOM.xlsx]
2018-01-31 Included plug adapter in BOM
    [BOM.xlsx]
2018-02-02 Included power board design and renamed circuit design files directory
    [BOM.xlsx, RTEP5.DSN, temp_sensor_blank.brd, temp_sensor_v1.brd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]
2018-02-07 Updated BOM. Updated Power PCB files. Reorganised Circuit Design Files
    [BOM.xlsx, RTEP5.DSN, gu-molex_0039281023.psm, gu-molex_0039281043.psm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]
2018-02-07 Added C file to read temp from sensor
2018-02-07 Did a few change to the Power PCB layout
    [RTEP5.DSN, layout1.brd]
2018-02-08 Finished Power PCB using Andrews footprints
    [RTEP5.DSN, gu-molex_0039281023.psm, gu-molex_0039281043.psm, gu-pi_gpio.psm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]
2018-02-09 Finished PCB and prepared for printing
    [RTEP5.DSN, layout1.brd, rhdrv4w140p420_550_2x2_960x9-1.psm, rhdrv4w140p550_420_2x2_960x9-1.psm]
2018-02-13 Moved BOM location
    [BOM.xlsx]
2018-02-21 Included wiring pi test PWM program and changes to temp sensor
2018-02-22 Update BOM after ordering heater and project box
    [BOM.xlsx]
2018-02-26 Added hole diagram for mechnical design
    [BOM.xlsx, RTEP5.DSN, layout1.brd, rhdrv2w140p420_550_2x1_960x5-1.psm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]
2018-02-27 Added hole diagram for heater box
2018-02-27 Updated heater box diagram
2018-03-06 Updated BOM.
    [BOM.xlsx]
2018-03-08 Created excel spreadsheet with graphs of the temperature rise and fall.
    [Temp Rise and Fall.xlsx]
2018-03-14 Updated repository readme file to include wiki information.
    [Temp Rise and Fall.xlsx]
2018-03-14 Included sample rate in the README
2018-03-15 Created a PID implementation which uses threads and minimizes busy waiting. Main has been updated to reflect these changes. CMakeLists has been updated to include the pthreads library.
2018-03-16 PID now fully implemented for a target ambient temperature. The code has yet to be compiled and tested. Functionally for calculating the duty cycle has been pushed into the PID controller.
2018-03-19 Included excel sheet for PID constant calculations
    [PID_constants_calculation.xlsx]
2018-03-19 Included overdamped PID results
    [overdamped_PID_results.xlsx]
2018-03-19 Completed overdamped temperature PID software
2018-03-20 Organised experimental data.
    [Full Power Up and Down.xlsx, PID Testing.xlsx, PID_constants_calculation.xlsx]
2018-03-20 Added final PID temperature controller results
2018-03-20 Added an excel document with graphs of the PID exprimental results. Updated BOM with missing components.
    [BOM.xlsx, PID Testing.xlsx]
2018-03-21 Added a function which selects the target ambient temperature based on the current neonate temperature
2018-03-23 created PDF copy of power schematic
2018-03-29 Included device images
2018-03-29 Included device image in README
2018-03-29 Included labelled device image for README
2018-03-29 Reduced device image size
2018-04-02 Integrated test GUI code, currently as two line plot, but is not connected to rest of program.
2018-04-03 added coupled code for GUI to control PID and read current temps
2018-04-16 Modified PCB image
2018-04-16 GUI has been implemented. PID updated with function to get target temperature.
2018-04-16 Swapped temperature sensors to be the right way round
2018-04-16 Included image of final device in README
